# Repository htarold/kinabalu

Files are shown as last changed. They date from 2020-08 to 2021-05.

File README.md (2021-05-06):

# What
This is the kinabalu recorder, a stereo autonomous passive audio
recorder.  We use it to record wildlife and environmental sounds
for research and conservation.

The boards/ directory contains design files for the recorder,
which will be needed to replicate the hardware.  All these
design files are licenced CC BY-SA 4.0.

# Hardware
The `boards/`
directory contains the design files; use `gEDA pcb`
and `gschem `
to modify them as desired.  All the hardware source files are CC-BY-SA-4.0.

If you wish to
replicate the boards, you'll want to zip the contents of the
    `boards/fab/`
directory (Gerbers and such) to send to the board house.  The `audio2`
board is the recorder proper; the `preamp2`
board is the stereo preamp for the microphones.  The version
here is for recording normal audio from electret condenser mics,
and it provides the requisite phantom power.
But you can make a custom preamp for other frequencies and
microphone types.

These are both 2-layer boards and very lax in their
requirements.  The usual 6/6 rules are more than sufficient.

The bills of materials allow for substantial flexibility in
sourcing the components, especially passives, so you can use
your favourite suppliers.

# Software

The `src/`
directory contains the source code that runs on the
recorder.  All these source files are licenced GPLv3 (if they
contain a main function) or LGPLv3 otherwise.  As it stands, use
`arm-none-eabi-gcc` and GNU `make`
to build.  You will also need to install `libopencm3`
available at [libopencm3](https://github.com/libopencm3/libopencm3).

The main target is `kinabalu.elf`
which you build as `make kinabalu.elf`
in the `src/` directory.

If you are running Windows, download and install
[FLASHER-STM32](https://www.st.com/en/development-tools/flasher-stm32.html)
from the microcontroller manufacturer (registration may
be needed).  `FLASHER-STM32` uses the
same USB-serial adapter (CH340 or equivalent) you use to talk to
the recorder, so you don't need to buy extra hardware.

This [video](https://www.youtube.com/watch?v=VDNJUsWvI0o)
(thanks Raul!) is a quick demo on using `FLASHER-STM32`.

If you are running Linux (Ubuntu etc.), then download and build
[stm32flash](https://github.com/stm32duino/stm32flash/tree/master).
You can use this command to upload the firmware:
```
$ stm32flash -w firmware.bin /dev/ttyUSB0
```
to upload `firmware.bin` via serial port `/dev/ttyUSB0`.

# Other hardware needed
In order to complete the recorder, you'll need the following:
- Micro SD card (8 to 64GB), FAT32 formatted.
- Lithium ion battery, 1S (3.7V) with JST-XH2 connector (Note
  polarity!).  A single 18650 is good for about 24 hours of
  recorded sound.
- CH340 or similar 3.3V USB-serial adapter.
- DS3231 RTC module, which you'll need to modify slightly (see
  [boards/README.md](boards/README.md)).
- Optionally a BME280 or BMP280 environmental sensor breakout.
- Optionally an STLINK V2 USB adapter for debugging.
- A weather proof housing to put everything in.

# Usage
The [sample config
file](https://github.com/htarold/kinabalu/blob/master/src/SITEA-0.LOG)
contains usage and troubleshooting instructions.

# Thanks
Comments and gripes to
htarold@gmail.com

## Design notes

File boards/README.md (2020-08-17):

# Schematic and layout
For hysterical reasons, the CAD files were generated using gEDA
`gschem` and `pcb` AKA geda-gaf.  I realise this isn't as popular as
`kicad` and if much further work were to be done on the boards, I
would probably convert them.  But artwork is provided in fab/.

# Components
## RTC
The board and schematic shows an RTC crystal, but the code does
not use this, so it is safe to not install the RTC crystal (and
load capacitors).

The on-board RTC is not used because in order to be useable it
would require a backup battery.  It is much simpler to use an
external off-the-shelf RTC with its own
backup battery.  You can search for "rtc raspberry pi DS3231"
in Aliexpress; these can be had for $1.

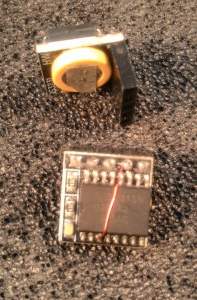
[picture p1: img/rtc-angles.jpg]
DS3231 RTC module intended for Raspberry Pis


This RTC however needs to be modified to be used.  The modification
involves soldering a bodge wire from pin 3 (#INT/SQW)  of the DS3231
to pin 4 of the socket header (which is not used by this
module, so we can use it).  This allows the DS3231 to generate
an alarm interrupt to wake the recorder board from deep sleep.

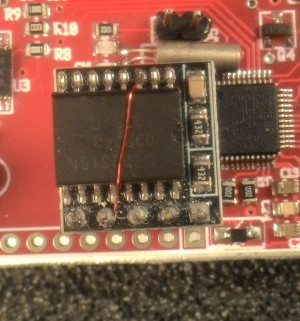
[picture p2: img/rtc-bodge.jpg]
Pin 3 of DS3231 must be tied to pin 4 of header


## I2C sensors
You can attach a BMP280 or BME280 environmental sensor to the
same I2C bus, to record air temperature and barometric pressure
(and relative humidity in the case of BME280).

## Substitutions
Some components may be substituted depending on requirements.

### Crystal oscillator/sample rate
In particular, the oscillator for the ADC is specced as 24.576MHZ,
and this is for sampling at 48 kHz.  The following is taken from
the PCM1808 datasheet:
Sampling Frequency:    Oscillator (clock) frequency:
8 kHz                   4.096 MHz
16 kHz                  8.192 MHz
32 kHz                  16.384 MHz
44.1 kHz                22.5792 MHz
48 kHz                  24.576 MHz
You can choose the proper oscillator frequency for your desired
sampling rate.  (The recorder has not been tested at sampling rates
higher than 48 kHz.)  Then edit src/Makefile to change the line
`DFLAGS+=-DWAV_SPS=44100`
to
`DFLAGS+=-DWAV_SPS=48000`
or whatever in order to match the oscillator actually installed
on your board.
You'll need to rebuild the kinabalu executable:
`$ make clean`
then:
`$ make kinabalu.bin`
from within the src/ directory.

If you reduce the sample rate, you are also limiting
the highest frequency you can make sense of to half that value
(e.g. 8 kHz sample rate means you can record up to 4 kHz sounds at
best) and you should also change the preamp filter to attenuate
anything higher than say 3kHz, certainly 4kHz.

You change the capacitor values to change the filter characteristics.
You could for instance specify a higher passband on one channel
and a lower one on the other.

Don't expect great filter performance, the attenuation of
the rejected frequencies will be noticeable but not stunning.
Also note the component tolerances are poor at perhaps 20%, so the
actual cutoff frequencies will be similarly off.

In many cases the stock filter values will suffice, and you can
digitally filter the files in post processing, which filters are
very much more capable anyway.  The preamp filters are used
mainly to avoid aliasing and to prevent very loud sounds in the
unwanted frequencies from completely swamping the ADC.  Digital
filters cannot help in that case.

The following shows the filter cutoff frequencies and the
corresponding capacitor values.  (Resistor values remain the
same in order to keep the pass band gain unchanged but you can
change these too if you know what you're doing.  But if you know
what you're doing you wouldn't be reading this).

There are 2 high pass filters per channel, and 2 low pass
filters per channel.  Each filter, whether high pass or low
pass, consists of a resistor and a capacitor, which in the table
below is referred to as Rlpf or Rhpf, and Clp or Chpf.  Within
the same channel, you should set both high pass filters to the same
frequency, and both low pass filters to the same frequency.

Keep Hz less than:         C2/C5/C11/C14
16 kHz                     120pF
6 kHz                      330pF
4 kHz                      470pF

And keep Hz greater than:  C4/C6/C13/C15
4 kHz                      4.7nF
2 kHz                      10nF
200 Hz                     100nF
20 Hz                      1uF

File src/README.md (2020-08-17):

# Build
You don't need to compile in order to programme the board, the
executable image is `src/kinabalu.bin` which you can programme to the
board.  You can skip to the Programming section to do this.

The build environment is plain make, under Ubuntu using
the GNU arm-none-eabi toolchain using the [libopencm3
library](https://github.com/libopencm3/libopencm3).  The Makefile takes
care of programming under stlink and under serial progamming.

The main make target is kinabalu.bin.  The other make targets
(named `test-*`) may be useful for debugging and testing but are not
necessary to build.

# Programming
As with all STM32 microcontrollers, this one can be programmed
using an STLINK-V2 programmer, or it can be programmed using the
builtin bootloader via the serial port.

Given that you will need a serial adapter to view the console
messages anyway, most people will probably opt to use this method.

## Serial programming option
(AKA uploading the programme to the microcontroller, AKA
flashing AKA burning.)
For this you'll need a serial adapter such as CH340, PL2303,
FT232, etc.  Make sure you set the I/O voltage to 3.3V on the
programmer, not 5V.  I use the CH340.

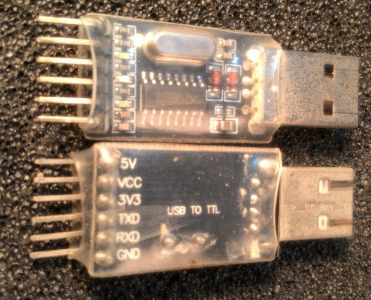
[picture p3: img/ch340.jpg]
CH340 USB-serial adapter


You'll also need a bit of software to programme the kinabalu.bin
image onto the chip.  Under Linux/Ubuntu (and probably Mac, I
can't vouch), I use [stm32flash](https://github.com/stm32duino/stm32flash)
Under Windows, you can [download the programmer software from
ST](https://www.st.com/en/development-tools/stm32cubeprog.html).
(free registration required).

You'll also need to place a jumper across J5, which will cause
the MCU to boot into the correct mode.  Lacking a jumper
you can use a paperclip to short the two pins of J5.

Connect the serial adapter to J1 on the board.  Note the
orientation, it goes ground-tx-rx-nc (the last pin is not
connected).

Connect the 1S battery to J6.  Note very carefully the polarity!
You can use a power supply set to 4V and the current limit
can be 100mA.

Power on the board (S1).

The image to use is `src/kinabalu.bin`.

Under Windows, start the ST-LINK Utility from ST and follow
their instructions.

Under Linux with `stm32flash`
in your path, you can issue the command:

`$ stm32flash -w kinabalu.bin <port>`

where `<port>` is the serial port connected to the serial adapter.

Remove the jumper/paperclip when done.

## STLINK V2 programming option
Most users will prefer to use serial programming (above) rather
than use the STLINK v2, because it
saves having to buy this programmer, which is useful mainly for
developers.

I have used the $2 stlink programmers from Aliexpress.  Search
for "stlink v2".  Be doubly careful with the pinouts when
attaching the connector, and make sure you use the 3.3V (not 5V)
output on the adapter.  The stlink adapter goes on to J2 on
the board.

Unlike programming using the serial adapter, the stlink adapter
power can be used to power the board during programming.
However the power switch (S1) must be turned on even if no external
power is used.  Turning it off shorts the stlink power
to ground (harmlessly).

[Programming software for the stlink v2
adapter](https://github.com/stlink-org/stlink).

With the adapter and board attached,
you can use the Makefile in `src/` to issue the command:

`$ make kinabalu.stflash`

# Testing
You'll need a FAT32 micro SD card.  Copy the sample
configuration file
`src/SITEA-0.LOG`
to it.  If you use a 64GB card, this usually comes formatted
EXFAT, so wll need to be reformatted.  This can be difficult to
do under Windows.

Attach the [modified RTC module](../boards/README.md) onto J4.

You can attach the preamp board with microphones to the audio board,
but this isn't necessary at this stage.

Optionally attach the serial adapter to J1 and set the comms
parameters to 57600 8N1.  This is to ubserve the diagnostics
output.

Turn on the board and observe the LEDs.  If the yellow LED comes
on and remains on, it probably means the RTC hasn't been
synchronised.  Follow the instructions on the console to set the
time, then reboot.

Otherwise the green LED (which indicates SD card activity)
should come on for 20 seconds, during which the board is
recording deployment notes.  You can speak into the microphones,
or if the preamp board is not attached, you can touch your
finger to pins 1 on J7 and J3 (marked L and R) to inject some
noise into the recorder.  After 20 seconds the recorder should
become dormant.

The configuration in `SITEA-0.LOG` tells the recorder to record
for 90 seconds every 2 minutes, so if you wait a few seconds the
recorder will wake up again to record for 90 seconds.  This
behaviour will repeat.

At any point (but preferably when the green LED is off) you can
power off the recorder and check the SD card.

Follow the notes in the `SITEA-0.LOG` file to change the recording
schedule.  There will also be diagnostics appended to that file
to verify correct operation.

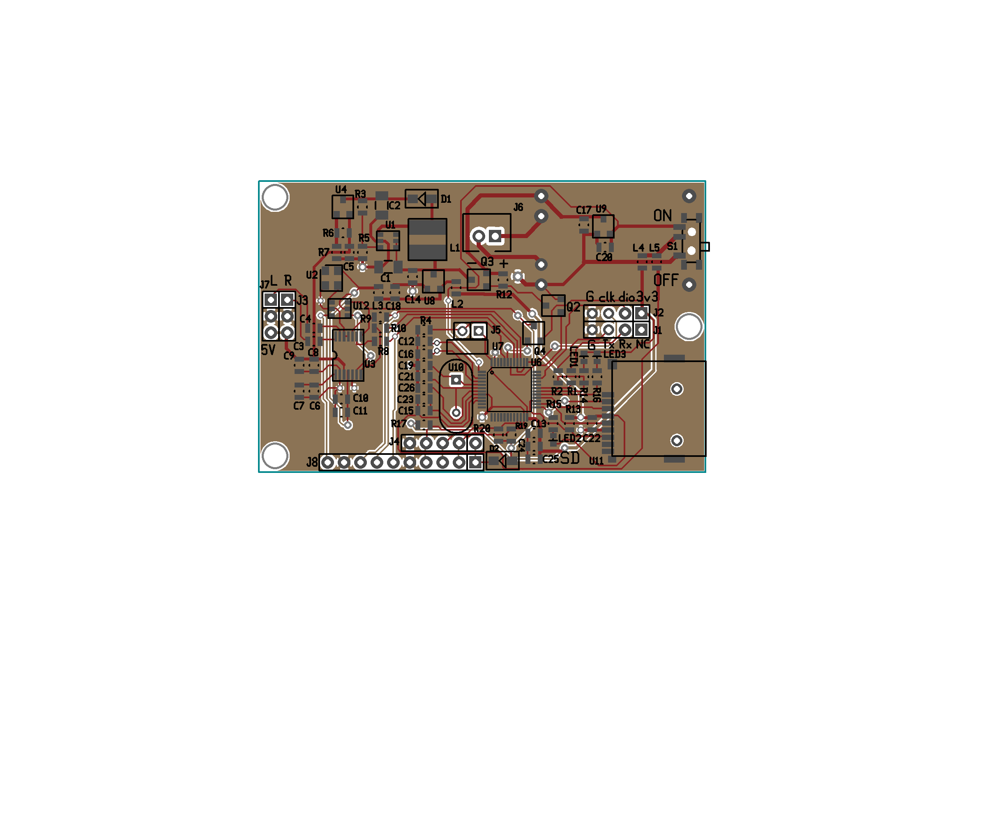
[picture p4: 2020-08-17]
boards/audio2.png

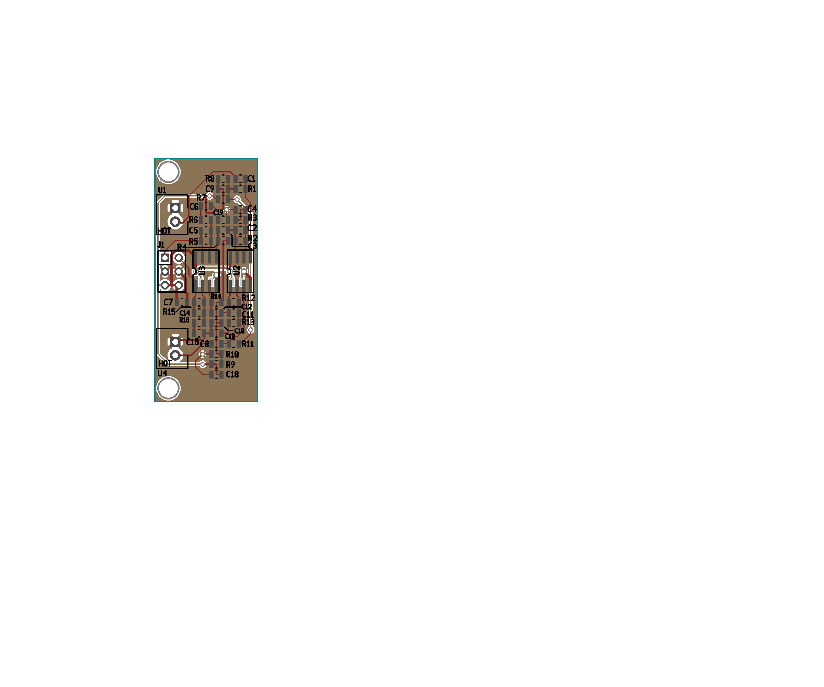
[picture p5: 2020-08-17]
boards/preamp2.pcb.png

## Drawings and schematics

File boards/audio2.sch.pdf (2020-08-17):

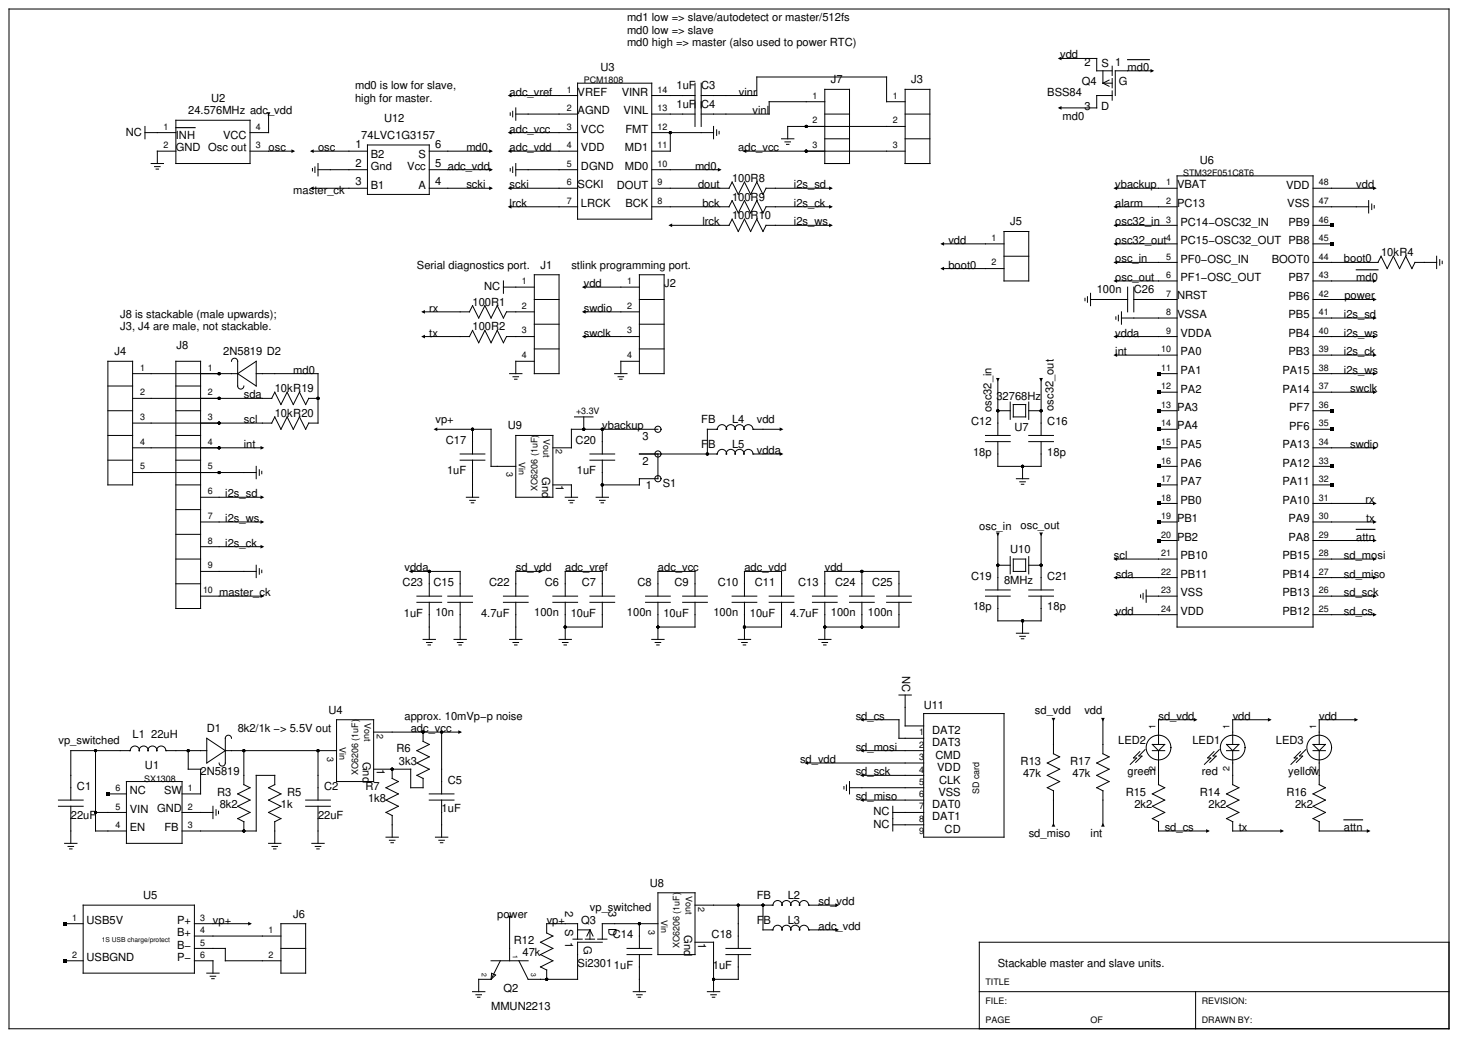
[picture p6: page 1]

md1 low => slave/autodetect or master/512fs
md0 low => slave
md0 high => master (also used to power RTC)

J8 is stackable (male upwards);
J3, J4 are male, not stackable.

3 | 3 scl

Stackable master and slave units.

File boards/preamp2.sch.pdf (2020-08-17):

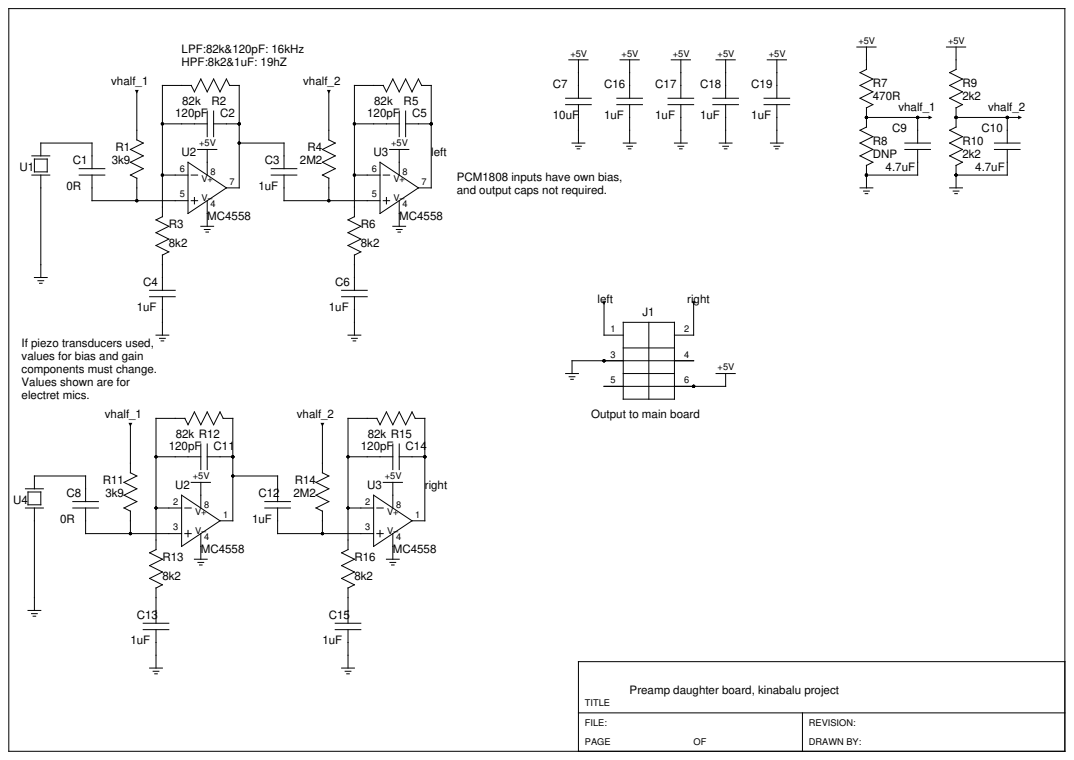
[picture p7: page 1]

PCM1808 inputs have own bias,
and output caps not required.

If piezo transducers used,
values for bias and gain
components must change.
Values shown are for
electret mics.

Output to main board

Preamp daughter board, kinabalu project

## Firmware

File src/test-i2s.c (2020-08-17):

/*
  Copyright 2020 Harold Tay GPLv3
  Test I2S.
 */

#include <libopencm3/stm32/rcc.h>
#include <libopencm3/stm32/gpio.h>
#include <libopencm3/stm32/usart.h>
#include <libopencm3/stm32/spi.h>
#include <libopencm3/stm32/flash.h>
#include <libopencm3/stm32/f0/nvic.h>
#include <libopencm3/stm32/exti.h>
#include <libopencm3/stm32/f0/spi.h>
#include <libopencm3/stm32/dma.h>
#include "tx.h"
#include "fmt.h"
#include "sd2.h"

#define MHZ 48
#include "delay.h"                    /* spin delay */

#define LED_PORT     GPIOC
#define LED_BIT      GPIO13
#define LED_RCC      RCC_GPIOC

#define TX_RCC       RCC_USART1
#define TX_PORT      GPIOA
#define TX_BIT       GPIO9
#define TX_AF        GPIO_AF1

#define RX_RCC       RCC_USART1
#define RX_PORT      GPIOA
#define RX_BIT       GPIO10
#define RX_AF        GPIO_AF1

#define I2S_SPI      SPI1
#define I2S_RCC      RCC_SPI1

#define I2S_WS_PORT  GPIOA
#define I2S_WS_BIT   GPIO15
#define I2S_WS_AF    GPIO_AF0

#define I2S_CK_PORT  GPIOB
#define I2S_CK_BIT   GPIO3
#define I2S_CK_AF    GPIO_AF0

#define I2S_MCK_PORT GPIOB
#define I2S_MCK_BIT  GPIO5
#define I2S_MCK_AF   GPIO_AF0

#define I2S_SD_PORT  GPIOB
#define I2S_SD_BIT   GPIO5
#define I2S_SD_AF    GPIO_AF0

#define I2S_WS2_PORT GPIOB
#define I2S_WS2_BIT  GPIO4

#define SD_SPI       SPI2
#define SD_SPI_RCC   RCC_SPI2

#define SD_CS_PORT   GPIOB
#define SD_CS_BIT    GPIO12
#define SD_CS_RCC    RCC_GPIOB

#define SD_SCK_PORT  GPIOB
#define SD_SCK_BIT   GPIO13
#define SD_SCK_AF    GPIO_AF0

#define SD_MISO_PORT GPIOB
#define SD_MISO_BIT  GPIO14
#define SD_MISO_AF   GPIO_AF0

#define SD_MOSI_PORT GPIOB
#define SD_MOSI_BIT  GPIO15
#define SD_MOSI_AF   GPIO_AF0

#define SETUP(port,bit,af,pupd) \
gpio_mode_setup(port, GPIO_MODE_AF, pupd, bit); \
gpio_set_af(port, af, bit);

static void rcc_setup(void)
{
  rcc_clock_setup_in_hse_8mhz_out_48mhz();
#if 1  /* for USART etc. Or, where to put this? XXX */
  rcc_periph_clock_enable(RCC_GPIOA);
  rcc_periph_clock_enable(RCC_GPIOB);
#endif
}

static void usart_setup(void)
{
  rcc_periph_clock_enable(RCC_USART1);
  SETUP(TX_PORT, TX_BIT, TX_AF, GPIO_PUPD_NONE)
  SETUP(RX_PORT, RX_BIT, RX_AF, GPIO_PUPD_NONE)
  usart_set_baudrate(USART1, 57600);
  usart_set_databits(USART1, 8);
  usart_set_parity(USART1, USART_PARITY_NONE);
  usart_set_stopbits(USART1, USART_CR2_STOPBITS_1);
  usart_set_mode(USART1, USART_MODE_TX_RX);
  usart_set_flow_control(USART1, USART_FLOWCONTROL_NONE);
  usart_enable(USART1);
}

/*
  At 48ksps, circbuf[1024] (2k of memory!) will be filled in 10.7ms,
  should be enough of a buffer.
 */
#define CIRCBUF_SIZE 1024
uint16_t circbuf[CIRCBUF_SIZE];
uint16_t circbuf_head;                /* Consume from here */
/*
  CNDTR contains the number of data yet to be transferred, so
  CIRCBUF_TAIL points to where the NEXT data will go.
 */
#define CIRCBUF_TAIL (CIRCBUF_SIZE-DMA_CNDTR(DMA1, DMA_CHANNEL2))

/*
  DMA setup XXX
  Using DMA only for I2S reception.
  I2S (=SPI1) rx can use channel 2.
  Configuration procedure (pg 191):
 */
static void dma_setup(void)
{
  rcc_periph_clock_enable(RCC_DMA1);
  dma_channel_reset(DMA1, DMA_CHANNEL2); /* Must use ch 2 */
  dma_set_peripheral_address(DMA1, DMA_CHANNEL2, (uint32_t)&SPI1_DR);
  dma_set_memory_address(DMA1, DMA_CHANNEL2, (uint32_t)circbuf);
  dma_set_number_of_data(DMA1, DMA_CHANNEL2, CIRCBUF_SIZE);
  dma_enable_circular_mode(DMA1, DMA_CHANNEL2);
  dma_set_read_from_peripheral(DMA1, DMA_CHANNEL2);
  dma_enable_memory_increment_mode(DMA1, DMA_CHANNEL2);
  dma_set_peripheral_size(DMA1, DMA_CHANNEL2, DMA_CCR_PSIZE_16BIT);
  dma_set_memory_size(DMA1, DMA_CHANNEL2, DMA_CCR_MSIZE_16BIT);
  dma_set_priority(DMA1, DMA_CHANNEL2, DMA_CCR_PL_VERY_HIGH);
  dma_enable_channel(DMA1, DMA_CHANNEL2);

  /* DMA_CNDTR2 contains the number of data remaining */
  circbuf_head = 0;
}

static void i2s_setup(void)
{
  /*
    force I2S to shut down first. XXX
   */
  while (SPI_SR(I2S_SPI) & (1<<7)) ;   /* BSY flag */
  SPI_I2SCFGR(I2S_SPI) &= ~(1<<10);
  delay_ms(1);

  dma_setup();

  rcc_periph_clock_enable(I2S_RCC);
  SETUP(I2S_WS_PORT, I2S_WS_BIT, I2S_WS_AF, GPIO_PUPD_NONE)
  SETUP(I2S_CK_PORT, I2S_CK_BIT, I2S_CK_AF, GPIO_PUPD_NONE)
  SETUP(I2S_SD_PORT, I2S_SD_BIT, I2S_SD_AF, GPIO_PUPD_NONE)
  gpio_mode_setup(I2S_WS2_PORT, GPIO_MODE_INPUT, GPIO_PUPD_NONE, I2S_WS2_BIT);
  /*
    I2S will be half-duplex, slave (PCM1808 provides the clocks).
    Pg 785, "I2S Philips protocol waveform" confirms to PCM1808
    pg. 17 FMT is low.
    I2S must be active and enabled before WS becomes active:
    I2SE must be set to 1 when WS = 1.
    See pg. 797, section 28.7.7.
   */
  /* Set I2SMOD; choose I2SSTD, DATLEN, CHLEN, I2SCFG */
  /* SPI_CR1(SPI1) not used in I2S mode */
  /* SPI_CR2(SPI1) is used for interrupt and DMA flags */
  /*
    SPI_SR(SPI1) is used for frame error, busy, overrun,
    underrun, CHSIDE, TXE, RXNE
   */
  spi_enable_rx_dma(I2S_SPI);
  SPI_I2SCFGR(I2S_SPI) =
                /* settings for PCM1808, FMT = MD1 = 0, MD0 = 1 */
      (1<<11)   /* I2SMOD = I2S mode */
    | (1<<8)    /* I2SCFG = slave receive */
    | (0<<4)    /* I2SSTD = philips */
    | (0<<3)    /* CKPOL = 0? XXX works if 1 or 0. */
    | (0<<1)    /* DATLEN = 16 bits */
    | (1<<0)    /* CHLEN = 32 bits */
    ;

  /*
    Avoid frame errors, wait until WS rises.
   */
#define WS2_HIGH (GPIO_IDR(I2S_WS2_PORT) & I2S_WS2_BIT)
#define WS2_LOW (!(GPIO_IDR(I2S_WS2_PORT) & I2S_WS2_BIT))
  while (WS2_HIGH) ;
  while (WS2_LOW) ;
  SPI_I2SCFGR(I2S_SPI) |=
      (1<<10);  /* I2S enable, after other bits configed */
}


int8_t sd_spi_init(void)
{
  gpio_mode_setup(SD_CS_PORT, GPIO_MODE_OUTPUT,
    GPIO_PUPD_NONE, SD_CS_BIT);
  gpio_set(SD_CS_PORT, SD_CS_BIT);
  rcc_periph_clock_enable(SD_SPI_RCC);
  SETUP(SD_SCK_PORT, SD_SCK_BIT, SD_SCK_AF, GPIO_PUPD_NONE);
  SETUP(SD_MISO_PORT, SD_MISO_BIT, SD_MISO_AF, GPIO_PUPD_NONE);
  SETUP(SD_MOSI_PORT, SD_MOSI_BIT, SD_MOSI_AF, GPIO_PUPD_NONE);

  spi_set_unidirectional_mode(SD_SPI);
  spi_disable_crc(SD_SPI);
  spi_set_data_size(SD_SPI, SPI_CR2_DS_8BIT);   /* XXX change to 16? */
  spi_set_full_duplex_mode(SD_SPI);
  spi_enable_software_slave_management(SD_SPI);
  spi_set_nss_high(SD_SPI);
  spi_set_baudrate_prescaler(SD_SPI, SPI_CR1_BR_FPCLK_DIV_128);
  spi_set_master_mode(SD_SPI);
  spi_send_msb_first(SD_SPI);
  spi_set_clock_polarity_0(SD_SPI);
  spi_set_clock_phase_0(SD_SPI);
  spi_enable_ss_output(SD_SPI);
  spi_enable(SD_SPI);
  return(0);
}
void sd_go_fast(void)
{
  spi_set_baudrate_prescaler(SD_SPI, SPI_CR1_BR_FPCLK_DIV_4); /* XXX */
}
void sd_cs_hi(void) { GPIO_BSRR(SD_CS_PORT) = SD_CS_BIT; }
void sd_cs_lo(void) { GPIO_BSRR(SD_CS_PORT) = (SD_CS_BIT << 16); }
/* Only used for file operations, not multi block writes */
uint8_t sd_xfer(uint8_t x)
{
  while (!(SPI_SR(SD_SPI) & SPI_SR_TXE)) ;
  SPI_DR8(SD_SPI) = x;
  return(SPI_DR8(SD_SPI));
}

int
main(void)
{
  int i;
  uint16_t v;

  rcc_setup();
  usart_setup();
  for (i = 4; i > 0; i--) {
    delay_ms(800);
    tx_msg("Delay ", i);
  }
restart:
  i2s_setup();
  tx_puts("i2s setup\r\n");

  /*
    XXX clear ovr flag?
   */
#if 0
  v = SPI_DR(I2S_SPI); 
  v = SPI_SR(I2S_SPI);
  for ( ; ; ) {
    uint16_t sr;
    for ( ; ; ) {
      sr = SPI_SR(I2S_SPI);
      if (sr & SPI_SR_RXNE) break;
      if (sr & SPI_SR_OVR) break;
    }
    v = SPI_DR(I2S_SPI);
    tx_puthex32(v);
    tx_puts("\r\n");
  }
#else
  v = 0;
  for ( ; ; ) {
    if (SPI_SR(I2S_SPI) & (1<<8)) {   /* frame error */
      tx_puts("F ");
      goto restart;
    }
    if (SPI_SR(I2S_SPI) & SPI_SR_OVR) {
      /* clear the error */
      uint16_t tmp;
      tmp = SPI_DR(I2S_SPI);
      tmp = SPI_SR(I2S_SPI);
      tx_puts("O ");
      goto restart;
    }
#if 0
    if (CIRCBUF_TAIL > circbuf_head) {
      tx_putdec(circbuf_head); tx_putc(':');
      tx_putdec(circbuf[circbuf_head++]); tx_puts("\r\n");
    } else
      tx_puts("wait ");
#else
    if ((!v) && (CIRCBUF_TAIL >= (CIRCBUF_SIZE-2))) {
      tx_puts("#");
      v = 1;
    } else {
      v = 0;
    }
#endif
  }
#endif
}

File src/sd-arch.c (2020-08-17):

/*
  Copyright 2020 Harold Tay LGPLv3
  Arch-specific routines declared in sd2.h but defined here.
 */
#include <libopencm3/stm32/rcc.h>
#include <libopencm3/stm32/gpio.h>
#include <libopencm3/stm32/spi.h>
#define MHZ 48
#include "delay.h"

#undef DBG
#ifdef DBG
#include "tx.h"
#include "fmt.h"
#define dbg(x) x
#else
#define dbg(x) /* nothing */
#endif

static int sd_spi_prescaler;
#define SD_SPI_PRESCALER_SLOW  SPI_CR1_BR_FPCLK_DIV_128
#define SD_SPI_PRESCALER_FAST  SPI_CR1_BR_FPCLK_DIV_4

#define SD_SPI   SPI2
#define SD_RCC   RCC_SPI2

#define CS_RCC   RCC_GPIOB
#define CS_PORT  GPIOB
#define CS_BIT   GPIO12

#define SCK_PORT GPIOB
#define SCK_BIT  GPIO13
#define SCK_AF   GPIO_AF0

#define MISO_PORT GPIOB
#define MISO_BIT  GPIO14
#define MISO_AF   GPIO_AF0

#define MOSI_PORT GPIOB
#define MOSI_BIT  GPIO15
#define MOSI_AF   GPIO_AF0

/* LED is active low */
#ifdef HAVE_LED
#define LED_OFF  GPIO_BSRR(LED_PORT) = LED_BIT
#define LED_ON   GPIO_BSRR(LED_PORT) = LED_BIT << 16
#endif
#define CS_HIGH  GPIO_BSRR(CS_PORT) = CS_BIT
#define CS_LOW   GPIO_BSRR(CS_PORT) = CS_BIT << 16

int8_t sd_spi_init(void)              /* used by sd2.c */
{
  rcc_periph_clock_enable(CS_RCC);
  gpio_mode_setup(CS_PORT, GPIO_MODE_OUTPUT, GPIO_PUPD_PULLUP, CS_BIT);
  CS_HIGH;
  /* spi_reset(SD_SPI); */
  rcc_periph_clock_enable(SD_RCC);

  gpio_mode_setup(SCK_PORT, GPIO_MODE_AF, GPIO_PUPD_NONE, SCK_BIT);
  gpio_set_af(SCK_PORT, SCK_AF, SCK_BIT);

  gpio_mode_setup(MOSI_PORT, GPIO_MODE_AF, GPIO_PUPD_NONE, MOSI_BIT);
  gpio_set_af(MOSI_PORT, MOSI_AF, MOSI_BIT);

  gpio_mode_setup(MISO_PORT, GPIO_MODE_AF, GPIO_PUPD_NONE, MISO_BIT);
  gpio_set_af(MISO_PORT, MISO_AF, MISO_BIT);

  spi_set_unidirectional_mode(SD_SPI);
  spi_disable_crc(SD_SPI);
  spi_set_data_size(SD_SPI, SPI_CR2_DS_8BIT);
  spi_set_full_duplex_mode(SD_SPI);                          /* XXX? */
  spi_enable_software_slave_management(SD_SPI);
  spi_set_nss_high(SD_SPI);             /* Important! or SPI -> slave */
  spi_set_baudrate_prescaler(SD_SPI,
    sd_spi_prescaler = SD_SPI_PRESCALER_SLOW);  /* XXX? */
  spi_set_master_mode(SD_SPI);
  spi_send_msb_first(SD_SPI);
  spi_set_clock_polarity_0(SD_SPI);
  spi_set_clock_phase_0(SD_SPI);
  spi_enable_ss_output(SD_SPI);
  spi_enable(SD_SPI);

  dbg(tx_puts("sd_spi_init ok\r\n"));
  return(0);
}

void sd_spi_reset(void)
{
  spi_reset(SD_SPI);
  gpio_mode_setup(CS_PORT,   GPIO_MODE_INPUT, GPIO_PUPD_NONE, CS_BIT);
  gpio_mode_setup(MOSI_PORT, GPIO_MODE_INPUT, GPIO_PUPD_NONE, MOSI_BIT);
  gpio_mode_setup(MISO_PORT, GPIO_MODE_INPUT, GPIO_PUPD_NONE, MISO_BIT);
  gpio_mode_setup(SCK_PORT,  GPIO_MODE_INPUT, GPIO_PUPD_NONE, SCK_BIT);
}

uint8_t sd_xfer(uint8_t x)
{
  uint16_t i, j;

  /* spi_send8() */
  j = ((sd_spi_prescaler==SD_SPI_PRESCALER_FAST)?1:32);
  for ( ; j > 0; j--) {
    for (i = 30000; i > 0; i--) {
      if (SPI_SR(SD_SPI) & SPI_SR_TXE) goto send;
      SPI_CR1(SD_SPI) |= SPI_CR1_MSTR;
      SPI_CR1(SD_SPI) |= SPI_CR1_SPE;
    }
  }
#ifdef DBG
  tx_puts("sd_xfer timed out waiting for SPI_SR_TXE, sr = ");
  tx_puthex32(SPI_SR(SD_SPI));
  tx_puts(" CR1 = ");
  tx_puthex32(SPI_CR1(SD_SPI));
  tx_puts(" CR2 = ");
  tx_puthex32(SPI_CR2(SD_SPI));
  tx_puts("\r\n");
#endif
  /* XXX What next? */
send:
  SPI_DR8(SD_SPI) = x;

  /* spi_read8() */
  /*
    XXX Can hang here, even after hard reset (but ok if
    reflashed).
  while (!(SPI_SR(SD_SPI) & SPI_SR_RXNE)) ;
   */
  return(SPI_DR8(SD_SPI));
}
void sd_cs_hi(void) { CS_HIGH; }
void sd_cs_lo(void) { CS_LOW; }
void sd_delay(uint8_t i)
{
  for ( ; i > 0; i--) { delay_us(250); }
}
void sd_go_fast(void)
{
  spi_set_baudrate_prescaler(SD_SPI,
    sd_spi_prescaler = SD_SPI_PRESCALER_FAST);  /* XXX? */
}

void dump_spi_regs(void)
{
#ifdef DBG
  tx_puts("SPI_CR1="); tx_puthex32(SPI_CR1(SD_SPI)); tx_puts("\r\n");
  tx_puts("SPI_CR2="); tx_puthex32(SPI_CR2(SD_SPI)); tx_puts("\r\n");
  tx_puts("SPI_SR="); tx_puthex32(SPI_SR(SD_SPI)); tx_puts("\r\n");
#endif
}

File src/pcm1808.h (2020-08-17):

#ifndef PCM1808_H
#define PCM1808_H
#include <libopencm3/stm32/dma.h>
/*
  Copyright 2020 Harold Tay LGPLv3
  Data are added by DMA to pcm1808_buf[PCM1808_HEAD] (circular
  buffer) starting with PCM1808_HEAD = 0.  Read only behind it,
  not in front.  Values at odd indices are left channel, even
  are right.

  48ksps in stereo means 192000 bytes per second or 5.2us per
  byte.  2048 bytes => 10.6ms which should be plenty.
 */
#define PCM1808_BUFSZ 2560
extern uint16_t pcm1808_buf[PCM1808_BUFSZ];
#define PCM1808_HEAD (PCM1808_BUFSZ-DMA_CNDTR(I2S_DMA, I2S_CHANNEL))

/*
  Errors that might be returned
 */
#define PCM1808_SR_BUSY  -51
#define PCM1808_WS2_HIGH -52
#define PCM1808_WS2_LOW  -53

extern int8_t pcm1808_start(void);    /* also does set up */
extern void pcm1808_stop(void);

/*
  These used only in pcm1808.c, valid for stm32f051c8.
 */
#define I2S_SPI      SPI1
#define I2S_RCC      RCC_SPI1
#define I2S_DMA      DMA1
#define I2S_DMA_RCC  RCC_DMA1
#define I2S_CHANNEL  DMA_CHANNEL2

/* I2S word select pin (left/right channel) */
#define I2S_WS_PORT  GPIOA
#define I2S_WS_BIT   GPIO15
#define I2S_WS_AF    GPIO_AF0
#define I2S_WS_RCC   RCC_GPIOA

/* I2S bit clock pin */
#define I2S_CK_PORT  GPIOB
#define I2S_CK_BIT   GPIO3
#define I2S_CK_AF    GPIO_AF0
#define I2S_CK_RCC   RCC_GPIOB

/* I2S serial data pin */
#define I2S_SD_PORT  GPIOB
#define I2S_SD_BIT   GPIO5
#define I2S_SD_AF    GPIO_AF0
#define I2S_SD_RCC   RCC_GPIOB

/* Tied to WS in hardware so we can read it */
#define I2S_WS2_PORT GPIOB
#define I2S_WS2_BIT  GPIO4
#define I2S_WS2_RCC  RCC_GPIOB

#endif
